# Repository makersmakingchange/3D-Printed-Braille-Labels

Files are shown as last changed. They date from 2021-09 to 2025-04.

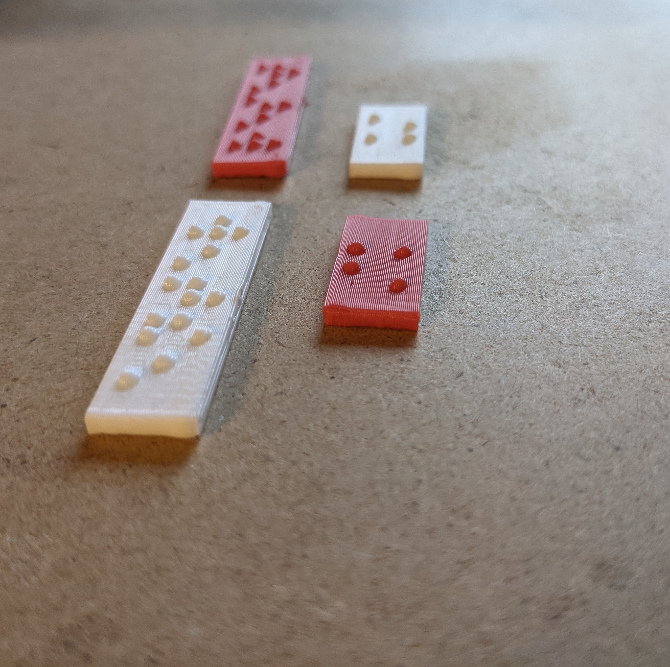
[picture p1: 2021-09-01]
Photos/side view.jpg

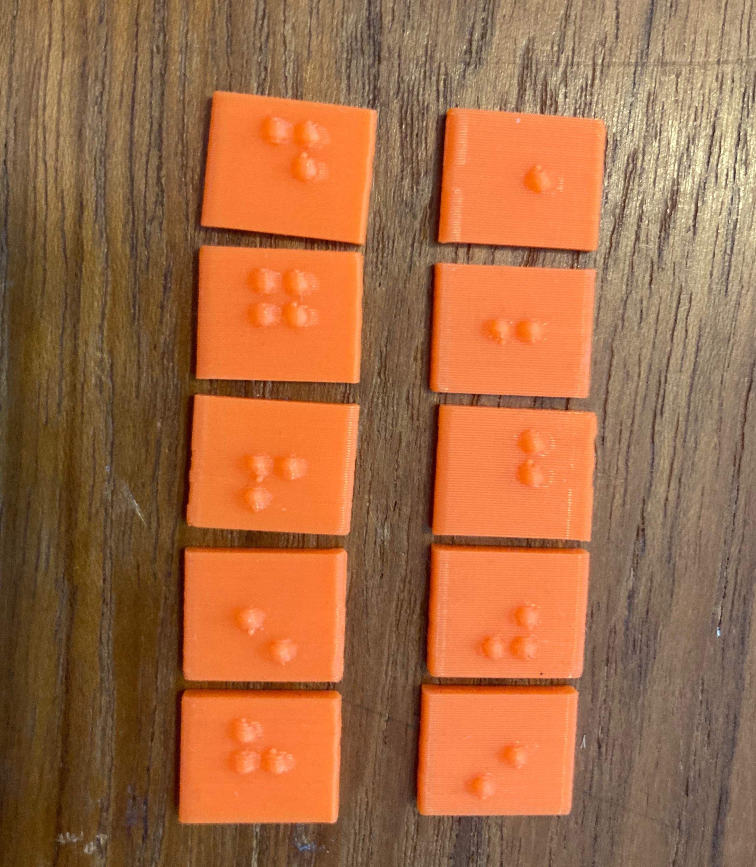
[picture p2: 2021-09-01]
Photos/braille_pic2.png

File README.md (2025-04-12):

# 3D Printed Braille Labels
Customizable 3D printed Braille Labels
# Documentation above includes: 
      - User Guide
      - 3D Print Guide
      - OpenSCAD Template
      - ChangeLog
      - Maker Checklist (use this if you are a maker to see the process of the build)
      - 3D Printed Braille Label STL examples such as the alphabet and numbers

# Overview

The OpenSCAD Braille font module allows an individual to customize and create 3D printable labels with Braille. 3D printed Braille is easy to print, does not take long, and requires little filament. Braille labels can be added to existing devices to increase accessibility or printed for the user's specific needs.

The OpenSCAD file can create properly spaced and standardized Braille letters, NEMETH numbers, mathematical operators, and some common contractions. Instructions on how to use the OpenSCAD program to create these labels are explained in the documentation of this project.

# Usage

The 3D printed Braille labels are intended to be used in the same way as standard Braille. The Braille labels can be glued or stuck to various surfaces. The Braille labels can also be incorporated in other 3D printed models as well, for example, on the side of another assistive device such as a switch.

# Build Instructions

The documentation includes an explainer document and video on how to use the OpenSCAD Braille template. If you are fulfilling this request for a requestor please take a look at the maker checklist document before you start the build to help you walk through the process.

SKILLS REQUIRED:

- 3D printing

TIME REQUIRED:

- Depends on how many Braille labels are needed but approx <10 mins per label

TOOLS:

- 3D printer
- OpenSCAD Software (free) [https://openscad.org/downloads.html]

3D PRINTING:

- See the 3D printing guide document for recommendations for printing Braille.

# Attribution

Michael Cantino and Sean Tikkun

<!-- ABOUT MMC START -->
## About Makers Making Change
[Makers Making Change Logo](https://www.makersmakingchange.com/)

Makers Making Change is a program of [Neil Squire](https://www.neilsquire.ca/), a Canadian non-profit that uses technology, knowledge, and passion to empower people with disabilities.

Makers Making Change leverages the capacity of community based Makers, Disability Professionals and Volunteers to develop and deliver affordable Open Source Assistive Technologies.

 - Website: [www.MakersMakingChange.com](https://www.makersmakingchange.com/)
 - GitHub: [makersmakingchange](https://github.com/makersmakingchange)
 - Bluesky: [@makersmakingchange.bsky.social](https://bsky.app/profile/makersmakingchange.bsky.social)
 - Instagram: [@makersmakingchange](https://www.instagram.com/makersmakingchange)
 - Facebook: [makersmakechange](https://www.facebook.com/makersmakechange)
 - LinkedIn: [Neil Squire Society](https://www.linkedin.com/company/neil-squire-society/)
 - Thingiverse: [makersmakingchange](https://www.thingiverse.com/makersmakingchange/about)
 - Printables: [MakersMakingChange](https://www.printables.com/@MakersMakingChange)

### Contact Us
For technical questions, to get involved, or to share your experience we encourage you to [visit our website](https://www.makersmakingchange.com/) or [contact us](https://www.makersmakingchange.com/s/contact).
<!-- ABOUT MMC END -->

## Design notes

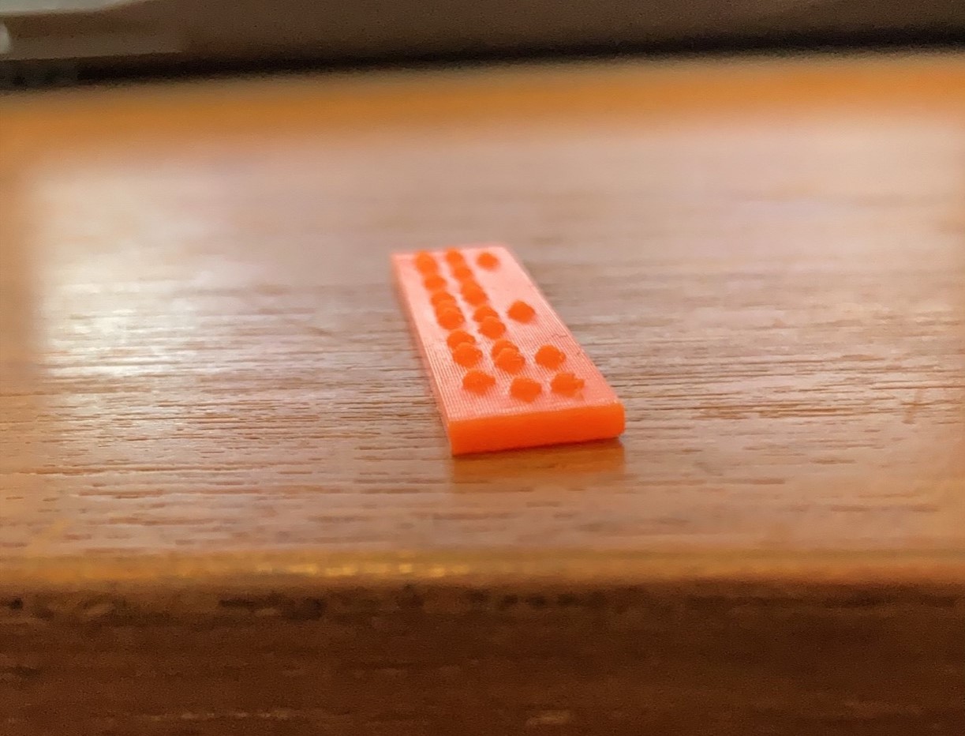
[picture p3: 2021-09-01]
Photos/braille_pic.png

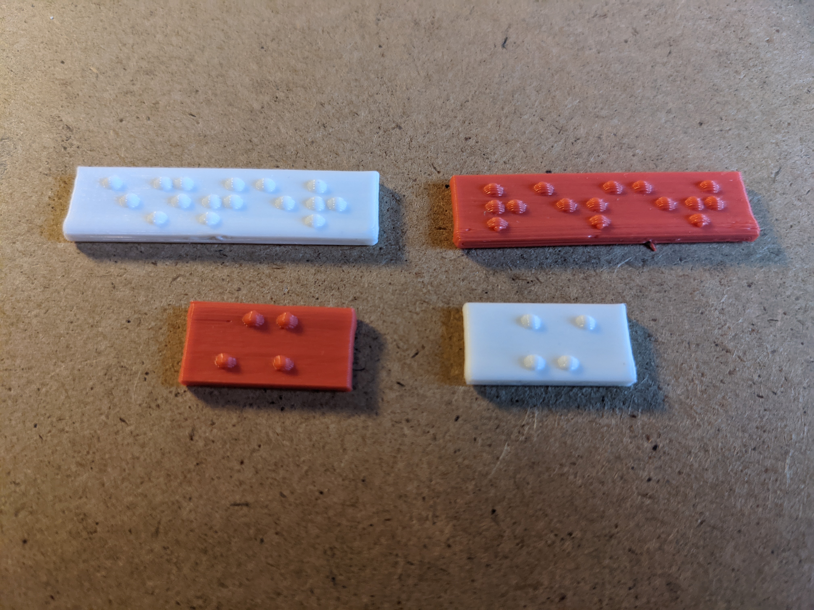
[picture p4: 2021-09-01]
Photos/long_small_braille.jpg

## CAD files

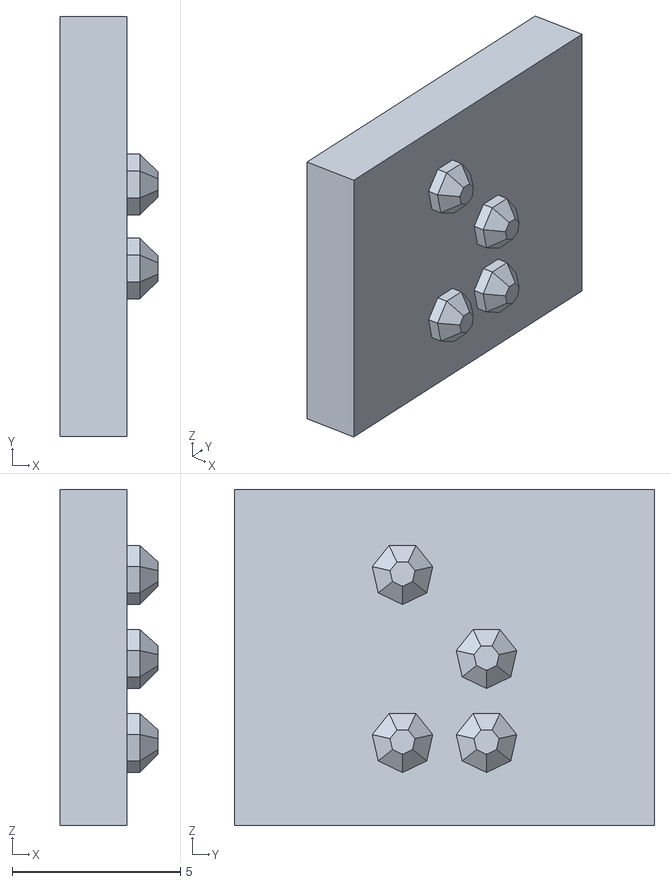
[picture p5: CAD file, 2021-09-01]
STL Library/Alphabet/Z.stl
2.92 x 12.5 x 10.0

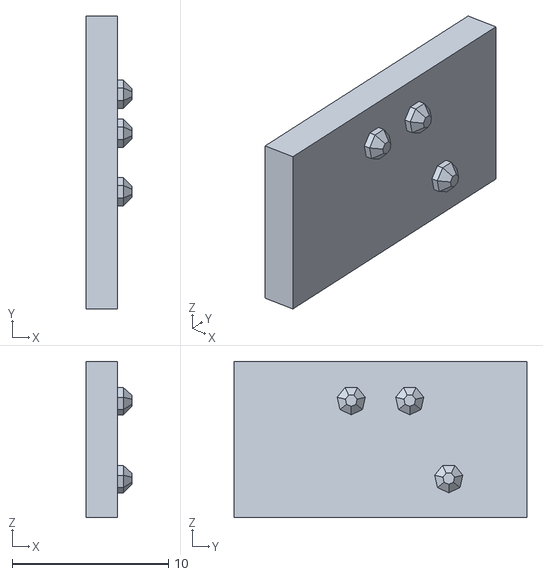
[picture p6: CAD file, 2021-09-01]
STL Library/math opperators/nemeth_multiplication_sign.stl
2.92 x 18.8 x 10.0

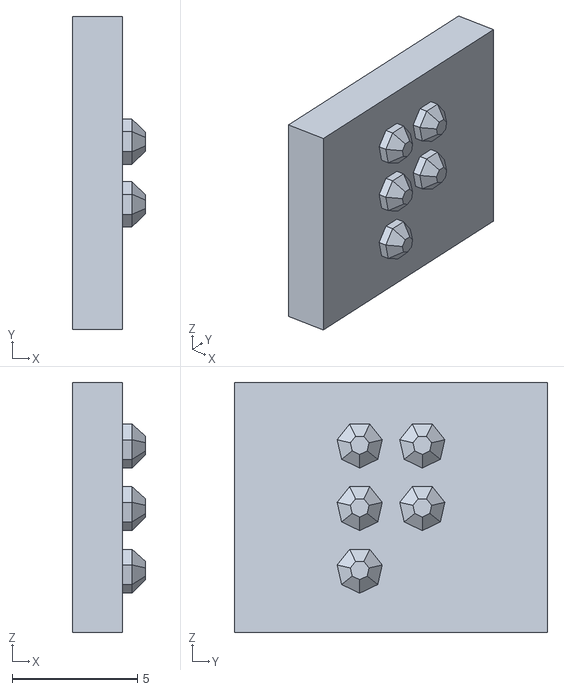
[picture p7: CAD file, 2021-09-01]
STL Library/Alphabet/Q.stl
2.92 x 12.5 x 10.0

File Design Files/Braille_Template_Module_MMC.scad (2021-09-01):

/*
Braille Module
http://creativecommons.org/licenses/by/3.0/
*/


// mm sizes from http://dots.physics.orst.edu/gs_layout.html
radius = 0.25;
spacing = 2.5;
distance = 3.75 + spacing;

plate_height = 10;
plate_thickness = 2;

$fn = 7;



module letter(bitmap) {
	row_size = 2;
	col_size = 3;
	bitmap_size = row_size * col_size;
	
	function loc_x(loc) = floor(loc / row_size) * spacing + spacing;
	function loc_y(loc) = loc % row_size * spacing  + (distance-spacing)/2;

	for (loc = [0:bitmap_size - 1]) {
		if (bitmap[loc] != 0) {
			union() {
				translate(v = [loc_x(loc), loc_y(loc), 0]) {
					sphere(radius = radius* bitmap[loc], center = true);
				}
			}
		}
	}
}


module braille_char(char) {
	if (char == "A") {
		letter([
			1,0,
			0,0,
			0,0
		]);
	} else if (char == "B") {
		letter([
			1,0,
			1,0,
			0,0
		]);
	} else if (char == "C") {
		letter([
			1,1,
			0,0,
			0,0
		]);
	} else if (char == "D") {
		letter([
			1,1,
			0,1,
			0,0
		]);
	} else if (char == "E") {
		letter([
			1,0,
			0,1,
			0,0
		]);
	} else if (char == "F") {
		letter([
			1,1,
			1,0,
			0,0
		]);
	} else if (char == "G") {
		letter([
			1,1,
			1,1,
			0,0
		]);
	} else if (char == "H") {
		letter([
			1,0,
			1,1,
			0,0
		]);
	} else if (char == "I") {
		letter([
			0,1,
			1,0,
			0,0
		]);
	} else if (char == "J") {
		letter([
			0,1,
			1,1,
			0,0
		]);
	} else if (char == "K") {
		letter([
			1,0,
			0,0,
			1,0
		]);
	} else if (char == "L") {
		letter([
			1,0,
			1,0,
			1,0
		]);
	} else if (char == "M") {
		letter([
			1,1,
			0,0,
			1,0
		]);
	} else if (char == "N") {
		letter([
			1,1,
			0,1,
			1,0
		]);
	} else if (char == "O") {
		letter([
			1,0,
			0,1,
			1,0
		]);
	} else if (char == "P") {
		letter([
			1,1,
			1,0,
			1,0
		]);
	} else if (char == "Q") {
		letter([
			1,1,
			1,1,
			1,0
		]);
	} else if (char == "R") {
		letter([
			1,0,
			1,1,
			1,0
		]);
	} else if (char == "S") {
		letter([
			0,1,
			1,0,
			1,0
		]);
	} else if (char == "T") {
		letter([
			0,1,
			1,1,
			1,0
		]);
	} else if (char == "U") {
		letter([
			1,0,
			0,0,
			1,1
		]);
	} else if (char == "V") {
		letter([
			1,0,
			1,0,
			1,1
		]);
	} else if (char == "W") {
		letter([
			0,1,
			1,1,
			0,1
		]);
	} else if (char == "X") {
		letter([
			1,1,
			0,0,
			1,1
		]);
	} else if (char == "Y") {
		letter([
			1,1,
			0,1,
			1,1
		]);
	} else if (char == "Z") {
		letter([
			1,0,
			0,1,
			1,1
		]);
	} else if (char == "CH") {
		letter([
			1,0,
			0,0,
			0,1
		]);
	} else if (char == "SH") {
		letter([
			1,1,
			0,0,
			0,1
		]);
	} else if (char == "TH") {
		letter([
			1,1,
			0,1,
			0,1
		]);
	} else if (char == "WH") {
		letter([
			1,0,
			0,1,
			0,1
		]);
	} else if (char == "OU") {
		letter([
			1,0,
			1,1,
			0,1
		]);
	} else if (char == "ST") {
		letter([
			0,1,
			0,0,
			1,0
		]);
	} else if (char == "AND") {
		letter([
			1,1,
			1,0,
			1,1
		]);
	} else if (char == "FOR") {
		letter([
			1,1,
			1,1,
			1,1
		]);
	} else if (char == "OF") {
		letter([
			1,0,
			1,1,
			1,1
		]);
	} else if (char == "THE") {
		letter([
			0,1,
			1,0,
			1,1
		]);
	} else if (char == "WITH") {
		letter([
			0,1,
			1,1,
			1,1
		]);
	} else if (char == "IN") {
		letter([
			0,0,
			0,1,
			1,0
		]);
	} else if (char == "EN") {
		letter([
			0,0,
			1,0,
			0,1
		]);
	} else if (char == "CON") {
		letter([
			0,0,
			1,1,
			0,0
		]);
	} else if (char == "DIS") {
		letter([
			0,0,
			1,1,
			0,1
		]);
	} else if (char == "COM") {
		letter([
			0,0,
			0,0,
			1,1
		]);
	} else if (char == "BE") {
		letter([
			0,0,
			1,0,
			1,0
		]);
	} else if (char == "EA") {
		letter([
			0,0,
			1,0,
			0,0
		]);
	} else if (char == "BB") {
		letter([
			0,0,
			1,0,
			1,0
		]);
	} else if (char == "CC") {
		letter([
			0,0,
			1,1,
			0,0
		]);
	} else if (char == "DD") {
		letter([
			0,0,
			1,1,
			0,1
		]);
	} else if (char == "FF") {
		letter([
			0,0,
			1,1,
			1,0
		]);
	} else if (char == "GG") {
		letter([
			0,0,
			1,1,
			1,1
		]);
	} else if (char == "AR") {
		letter([
			0,1,
			0,1,
			1,0
		]);
	} else if (char == "BLE") {
		letter([
			0,1,
			0,1,
			1,1
		]);
	} else if (char == "ED") {
		letter([
			1,1,
			1,0,
			0,1
		]);
	} else if (char == "ER") {
		letter([
			1,1,
			1,1,
			0,1
		]);
	} else if (char == "GH") {
		letter([
			1,0,
			1,0,
			0,1
		]);
	} else if (char == "ING") {
		letter([
			0,1,
			0,0,
			1,1
		]);
	} else if (char == "OW") {
		letter([
			0,1,
			1,0,
			0,1
		]);
	} else if (char == "cap") {
		letter([
			0,0,
			0,0,
			0,1
		]);
	} else if (char == "#") {
		letter([
			0,1,
			0,1,
			1,1
		]);
	} else if (char == ".") {
		letter([
			0,0,
			1,1,
			0,1
		]);
	} else if (char == "?") {
		letter([
			0,0,
			1,0,
			1,1
		]);
	} else if (char == "!") {
		letter([
			0,0,
			1,1,
			1,0
		]);
	} else if (char == "-") {
		letter([
			0,0,
			0,0,
			1,1
		]);
	} else if (char == "quote") {
		letter([
			0,0,
			0,1,
			1,1
		]);
	} else if (char == "1") {
		letter([
			1,0,
			0,0,
			0,0
		]);
	} else if (char == "2") {
		letter([
			1,0,
			1,0,
			0,0
		]);
	} else if (char == "3") {
		letter([
			1,1,
			0,0,
			0,0
		]);
	} else if (char == "4") {
		letter([
			1,1,
			0,1,
			0,0
		]);
	} else if (char == "5") {
		letter([
			1,0,
			0,1,
			0,0
		]);
	} else if (char == "6") {
		letter([
			1,1,
			1,0,
			0,0
		]);
	} else if (char == "7") {
		letter([
			1,1,
			1,1,
			0,0
		]);
	} else if (char == "8") {
		letter([
			1,0,
			1,1,
			0,0
		]);
	} else if (char == "9") {
		letter([
			0,1,
			1,0,
			0,0
		]);
	} else if (char == "0") {
		letter([
			0,1,
			1,1,
			0,0
		]);
        } else if (char == "dot4") {
		letter([
			0,1,
			0,0,
			0,0
		]);
        } else if (char == "dot5") {
		letter([
			0,0,
			0,1,
			0,0
		]);
        } else if (char == "dot45") {
		letter([
			0,1,
			0,1,
			0,0
		]);
         } else if (char == "dot456") {
		letter([
			0,1,
			0,1,
			0,1
		]);
        } else if (char == "dot56") {
		letter([
			0,0,
			0,1,
			0,1 
		]);
        } else if (char == "dot46") {
		letter([
			0,1,
			0,0,
			0,1 
		]);
        } else if (char == "n.") {
		letter([
			0,1,
			0,0,
			0,1 
		]);
        } else if (char == "grade1") {
		letter([
			0,0,
			0,1,
			0,1 
		]);
        } else if (char == "n1") {
		letter([
			0,0,
			1,0,
			0,0
		]);
	} else if (char == "n2") {
		letter([
			0,0,
			1,0,
			1,0
		]);
	} else if (char == "n3") {
		letter([
			0,0,
			1,1,
			0,0
		]);
	} else if (char == "n4") {
		letter([
			0,0,
			1,1,
			0,1
		]);
	} else if (char == "n5") {
		letter([
			0,0,
			1,0,
			0,1
		]);
	} else if (char == "n6") {
		letter([
			0,0,
			1,1,
			1,0
		]);
	} else if (char == "n7") {
		letter([
			0,0,
			1,1,
			1,1
		]);
	} else if (char == "n8") {
		letter([
			0,0,
			1,0,
			1,1
		]);
	} else if (char == "n9") {
		letter([
			0,0,
			0,1,
			1,0
		]);
	} else if (char == "n0") {
		letter([
			0,0,
			0,1,
			1,1
        ]);
    } else if (char == "+") {
		letter([
			0,1,
			0,0,
			1,1 
		]);
        
        } else if (char == "-") {
		letter([
			0,0,
			0,0,
			1,1 
		]);
            //for the next four characters (*1,*2,/1,/2) this stands for two two parts that need to be included for multiplication and divison. So if you want a multiplication symbol for examply you would input this: chars = ["*1","*2"]; since multplication and division needs two cells.
char_count = 2;
        } else if (char == "*1") {
		letter([
			0,1,
			0,0,
			0,0 
		]);
        } else if (char == "*2") {
		letter([
			1,0,
			0,0,
			0,1 
		]);
        } else if (char == "/1") {
		letter([
			0,1,
			0,0,
			0,1
		]);
         } else if (char == "/2") {
		letter([
			0,1,
			0,0,
			1,0
		]);
	} else {
		echo("Invalid Character: ", char);
	}

}

module braille_str(chars, char_count) {
	echo(str("Total Width: ", distance * char_count, "mm"));
	union() {
		for (count = [0:char_count-1]) {
			translate(v = [0, count * distance, plate_thickness]) {
				braille_char(chars[count]);
			}
		}
		translate(v = [0, -distance/2, 0]) {
			color([0,0,1]) {
				cube(size = [plate_height, distance * (char_count+1), plate_thickness]);
			}
		}
	}
}






chars = 
["T","E","S","T"];
char_count = 4;

union()
{
	rotate([0,90,0]) braille_str(chars, char_count);
	// uncomment next line to have a small "foot" added for better adhesion to the print platform or raft
	//translate([-19,20,-plate_height]) cube(size = [20,5,2]);
}

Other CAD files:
STL Library/numbers/nemeth_three.stl
STL Library/Alphabet/M.stl
STL Library/math opperators/nemeth_minus_sign.stl
STL Library/numbers/nemeth_zero.stl
STL Library/Alphabet/B.stl
STL Library/math opperators/nemeth_divison_sign.stl
STL Library/numbers/nemeth_five.stl
STL Library/Alphabet/T.stl
STL Library/math opperators/nemeth_plus_sign.stl
STL Library/numbers/nemeth_six.stl
STL Library/Alphabet/O.stl
STL Library/numbers/nemeth_two.stl
STL Library/numbers/nemeth_eight.stl
STL Library/Alphabet/Y.stl
STL Library/numbers/nemeth_nine.stl
STL Library/Alphabet/A.stl
STL Library/Alphabet/C.stl
STL Library/Alphabet/D.stl
STL Library/Alphabet/E.stl
STL Library/Alphabet/F.stl
STL Library/Alphabet/G.stl
STL Library/Alphabet/H.stl
STL Library/Alphabet/I.stl
STL Library/Alphabet/J.stl
STL Library/Alphabet/K.stl
STL Library/Alphabet/L.stl
STL Library/Alphabet/N.stl
STL Library/Alphabet/P.stl
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

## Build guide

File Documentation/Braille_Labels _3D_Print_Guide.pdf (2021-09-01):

V1.0 |<August> <2021>

## DIY Braille Labels

## 3D PRINTING GUIDE

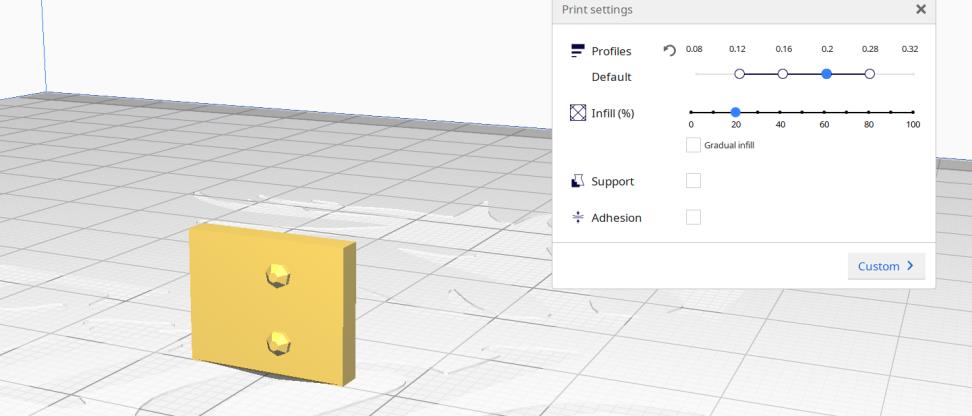
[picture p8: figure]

© 2021 by <Author>.
This work is licensed under the CC BY SA 4.0 License: http://creativecommons.org/licenses/by-sa/4.0
Files available at <Replace with MMC Library Link> | Page 1 of 2

### 3D Printing Summary

There are some best practices of 3D printing Braille. The optimal print settings can be found below but best practices to note are listed here:

- Print braille vertically (see photos below)
- Do not resize Braille or scale the 3D model. This will render the braille unreadable
- Limit the amount of Braille labels printed at once to eliminate stringing between labels

### 3D Printing Settings:

| Infill (%) | Material | Support(Y/N) | Layer Height/ Nozzle Diameter(mm) | Notes (orientation, special settings, etc)
Recommended Print settings | 20 | Tested with PLA | N | 0.2/0.4 | -Print in vertical orientation as seen here below

### Post-Processing

- If you notice any blobs on the side of the Braille tiles try using a blade to clean up the prints. Braille is hyper-specific so any bumps or abnormalities on the print that could affect readability should be removed.

### Customization Options

- The Braille labels should not be resized
- Color of Braille may matter to the individual if they are only partly visually impaired. Check with user

## DIY Braille Labels

## 3D PRINTING GUIDE

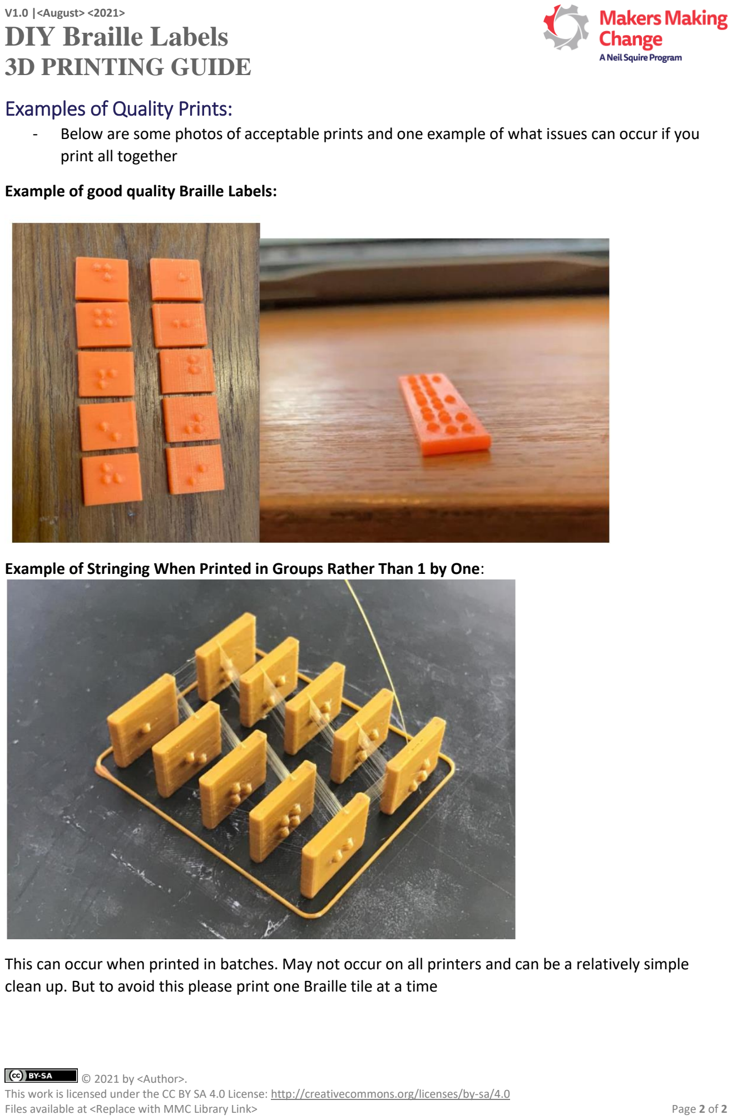
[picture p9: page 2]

V1.0 |<August> <2021>

© 2021 by <Author>.
This work is licensed under the CC BY SA 4.0 License: http://creativecommons.org/licenses/by-sa/4.0
Files available at <Replace with MMC Library Link> | Page 2 of 2

### Examples of Quality Prints:

- Below are some photos of acceptable prints and one example of what issues can occur if you print all together

Example of good quality Braille Labels:

Example of Stringing When Printed in Groups Rather Than 1 by One:

This can occur when printed in batches. May not occur on all printers and can be a relatively simple clean up. But to avoid this please print one Braille tile at a time

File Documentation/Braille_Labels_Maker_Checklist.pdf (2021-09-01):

V1.0 | <August> <2021>

## Braille Calculator

## MAKER CHECKLIST

© 2021 by <Author>.
This work is licensed under the CC BY SA 4.0 License: http://creativecommons.org/licenses/by-sa/4.0
Files available at <Replace with MMC Library Link> | Page 1 of 1

## Maker To Do List

Discuss any customization or special tweaks the user may need for the device. Ensure the best to your ability that the user knows what the device is for/how it will work.
Discuss with user the cost of materials (including possible shipping) of the components and agree on reimbursement
Print the Braille Labels
Deliver/send the labels to the requester
Contact user to let them know it is complete (update MMC forum request page if request was through there)

## Items to Give to User

Braille labels

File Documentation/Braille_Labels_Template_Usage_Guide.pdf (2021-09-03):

V1.0 | <August> <2021>

## Braille Labels

### OPENSCAD TEMPLATE GUIDE

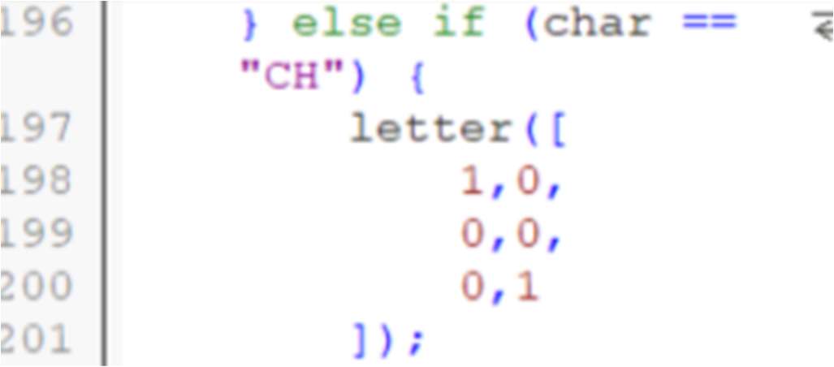
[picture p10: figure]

© 2021 by <Author>. This work is licensed under the CC BY SA 4.0 License: http://creativecommons.org/licenses/by-sa/4.0
Files available at <Replace with MMC Library Link> | Page 1 of 3

### Overview

The open source software OpenSCAD is used to create custom Braille labels. There is an OpenSCAD file (.scad) included on the GitHub page which is already set up to create Braille label STL’s based off of the inputted characters. There is no modeling, programming, or prior CAD knowledge necessary when using this OpenSCAD template. The steps to create custom label STL’s can be found below.

Note: There is also a video included on the GitHub page that walks you through the same process.

Note: Do not resize the Braille as it may render it unreadable.

### Creating Braille Labels from Template:

### Step 1: Downloading OpenSCAD

- The download link for OpenSCAD can be found here: https://openscad.org/downloads.html
- The software is free and available on Windows, MacOS, and Linux

### Step 2: Open the OpenSCAD Braille Template File

- Once OpenSCAD is downloaded, locate the “Braille_Template_Module_MMC.scad” file on the GitHub page and double click it to open the file in OpenSCAD.

### Step 3: Finding Available Characters, numbers, signs, and contractions

- On the left side of the screen, there is a text pane where the code that creates the template is located.
- When you scroll down you will come across a large section that has a lot of “else if” statements like shown in the below figure.
- Each character, number, sign, or contraction is shown in quotations and below that a series of 1’s and 0’s are used to control the braille dots. A 1 adds a braille dot in that part of the cell. A 0 has no dot.

V1.0 | <August> <2021>

## Braille Labels

### OPENSCAD TEMPLATE GUIDE

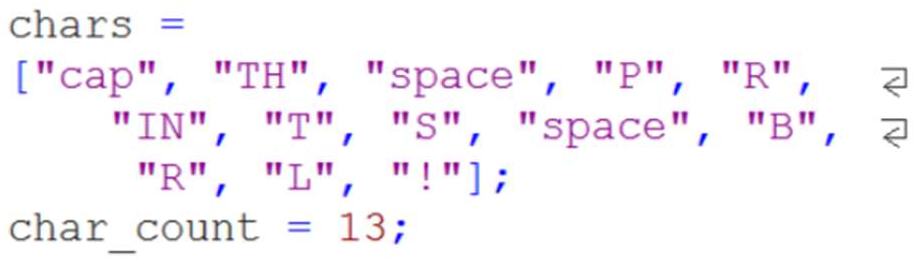
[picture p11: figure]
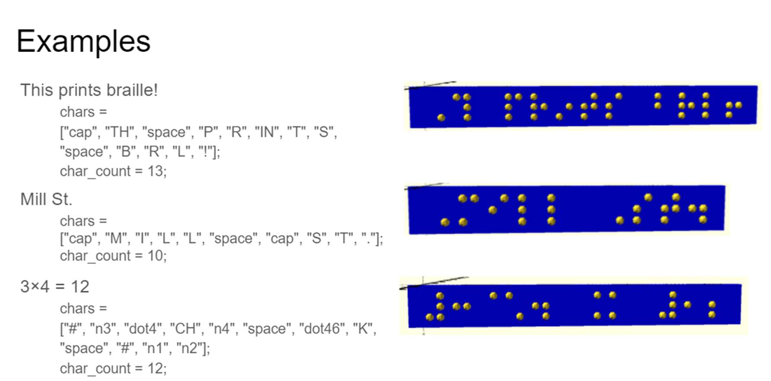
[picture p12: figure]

Files available at <Replace with MMC Library Link> | Page 2 of 3
- Scrolling through the text on the left side you will be able to see all of the available characters that are available in this document. There is potential to add characters. This is described later in this document.

### Step 4: Entering Text

- In the text pane on the left side of the screen, you will see all the programming used to build the tool. At the bottom of the text field (line 662-665), you will find an area to edit the braille shown below:
- All characters must be enclosed in quotation marks. Letters and contractions must be capitalized. Commas are used before any new cell added. Note that there should be no comma on the last character before the square bracket is closed.
- Enter the number of characters you’re using after “char_count = ” . As shown in the example above there is 13 characters in the desired input and therefore the user has input the character input to 13. Further examples can be seen below:

V1.0 | <August> <2021>

## Braille Labels

### OPENSCAD TEMPLATE GUIDE

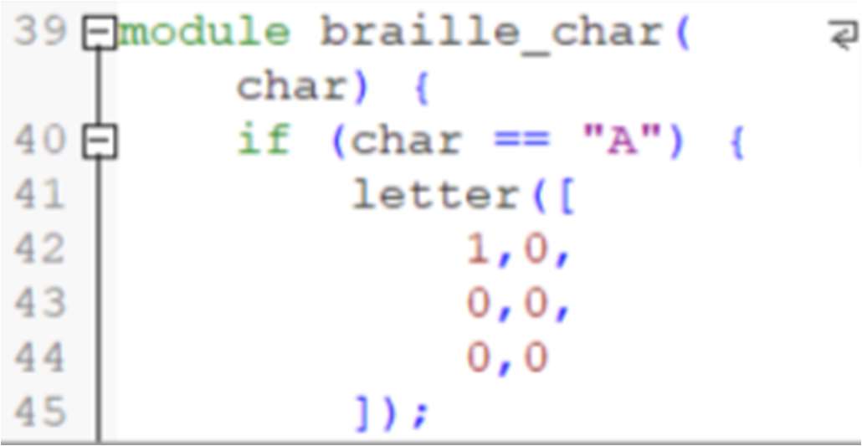
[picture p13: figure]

Files available at <Replace with MMC Library Link> | Page 3 of 3

### Step 5: Creating the 3D Printable Braille Model

- Once step 4 is complete and you are happy with the text you have entered, click on the “Preview” button at the top of the text pane to view your model. This looks like a cube with two arrows going to the right.
- If everything looks correct and the model loads without error, click the “Render” button to prepare your model. If you’re not ready, make the necessary edits and then hit “Preview” again.
- After rendering the model, you’re ready to export the file. Click on the “Export as STL” button and save the file. This file can now be used to 3D print. Please see 3D Printing Guide document for tips on printing Braille.

### Adding New Characters to the Current Template:

If you cannot find the letter, number, or contraction you are looking for in the template and want to create your own, please follow this method:

- Copy one of the already defined characters starting with the line that says “module” until the next semicolon and paste it after the code for an existing character. For example, you would copy a section like the one below:
- Edit the character name in the quotes, and alter the braille dots by using 1’s and 0’s. 1’s will be the location where the Braille dots are and 0’s will be empty space.

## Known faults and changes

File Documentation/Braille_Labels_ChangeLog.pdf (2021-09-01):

V1.0 | <August> <2021>

## Braille Labels

## CHANGELOG

© 2021 by <Author>. This work is licensed under the CC BY SA 4.0 License: http://creativecommons.org/licenses/by-sa/4.0
Files available at <Replace with MMC Library Link> | Page 1 of 1

## Version 0.0 | Date 2019

This is a remix and expansion of the OpenSCAD braille module posted by Sean Tikkun and drayed. Michael Cantino expanded a OpenSCAD Braille font module that can be found at this link (https://www.thingiverse.com/thing:3490757). Michael created a forum link (https://forum.makersmakingchange.com/t/3d-printed-braille/1248/2) that discussed his expertise in Braille and open source options to create devices for people living with visual impairment such as Braille labels, tactile maps, and others.

This OpenSCAD document is able to create Braille labels of:

- Numbers
- Letters
- These “dot#” characters are the only characters not included in the original module. They allow for complete transcription of any text into braille.
- Nemeth Numbers – These characters were all included as a contraction or punctuation in the original module. For ease of use when creating Nemeth text, redundant characters were added for Nemeth numbers and symbols. Symbol “n.” is a Nemeth decimal.

## Version 1.0 | Date 08/2021

The R&D team at Makers Making Change took the V0.0 devices Braille font module and used it in the Braille Calculator device. This required the team to expand the font module to include the mathematical operators and provide documentation on recommended print settings. Therefore in this version the module has been expanded to include addition, subtraction, multiplication, and division.
